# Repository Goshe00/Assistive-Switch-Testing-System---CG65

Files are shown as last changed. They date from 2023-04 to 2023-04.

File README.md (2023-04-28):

 <!--- 
TITLE
Should match the name of the GitHub repository. Choose something descriptive rather than whimsical. 
 --->
 # Assistive Switch Testing System - CG65

<!--- 
SUMMARY
A brief summary of the project. What it does, who it is for, how much it costs.
 --->
We are from UBC ECE Capstone Group CG65 and our project is to build a cost-effective test system for engineers to test the assistive switch for Neil Squire's Program Makers Making Change. The testing system is made from modifying a commercially available 3D printer, low cost electrical components, 3D printed parts and specially designed user interface.

<!--- 
PHOTO

 --->
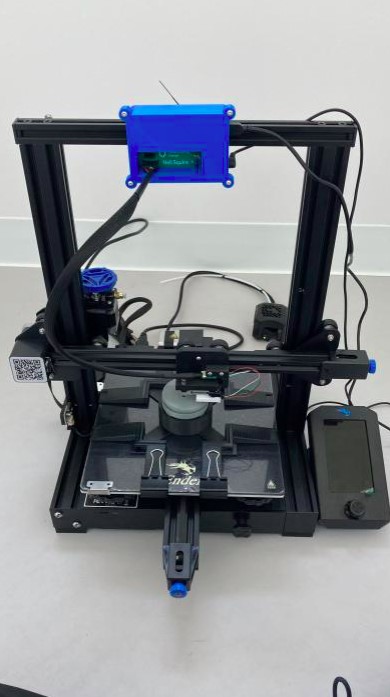
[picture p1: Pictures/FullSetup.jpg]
Assistive Switch Testing System Full Setup


<!--- 
## More info at
 - [Makers Making Change Forum Thread](TBD) 
 - [Makers Making Change Project Page](TBD)
 --->

## Getting Started
<!--- 
Include an overall idea of what major steps are required to build the device.
 --->

### 1. Order the 3D printer
Our testing system will be assembled on a 3D printer. For our project, we've chosen the Ender 3 V2 from [3D Printing Canada](https://3dprintingcanada.com/products/creality-ender-3-v2) since it is CSA and ETL safety certified. So far, this testing system has been implemented on an Ender 3 V2 and you can acquire the same model from any available store.

### 2. Order and assemble the activation circuit
The activation circuit will be used to receive and send signals from the load cell and switch to a computer.

All of the files and documentation can be found in the [/Electronics/Activation_Circuit/PCB_Assembly_Guide.pdf](https://github.com/Goshe00/Assistive-Switch-Testing-System---CG65/tree/main/Electronics/Activation%20Circuit) folder.

### 3. Order and assemble the force sensor

The force sensor includes the load cell and its adapter. It will be used to send signals to the PCB during a testing routine.

All of the documentation can be found in the [/Electronics/Force Sensor](https://github.com/Goshe00/Assistive-Switch-Testing-System---CG65/tree/main/Electronics/Force%20Sensor) folder. Individual print files of the adapter can be found in [/3D_Printing_Files/Load_Cell_Adapter](https://github.com/Goshe00/Assistive-Switch-Testing-System---CG65/tree/main/3D%20Printing%20Files/Load%20Cell%20Adapter) folder. The code to configure the microcontroller can be found in [/Software/ESP](https://github.com/Goshe00/Assistive-Switch-Testing-System---CG65/tree/main/Software/ESP32)

### 4. Install and setup Neoprint, our testing system's user interface

Neoprint is a Python program specifically for this testing system that enables the user to set up, run test routines and generate data. 

All of the build documentation and files can be found in the [/Software/Neoprint](/Software/Neoprint) folder. 

### 5. Assemble the force sensor, activation circuit and Neoprint

After assembling and setting up each of the subcomponents, they can be assembled together to build the testing system.

User guides of each subcomponents can be found in their respective folders. 

### 6. Assemble the switch 

The testing procedure starts by deciding which switch is needed to be tested. For this project, we have implemented a testing procedure for the MMC60 switch. 

### 7. Print and assemble the switch adapter

In order for the switch to be fixed on the printbed, an adapter is needed to hold the switch so that it does not move or rotate during testing.

All individual print files and documentation of MMC60 switch and Interact switch can be found in [/3D_Printing_Files/MMC60_Jig](https://github.com/Goshe00/Assistive-Switch-Testing-System---CG65/tree/main/3D%20Printing%20Files/MMC60%20Jig) folder and [/3D_Printing_Files/Interact_Switch_Jig](https://github.com/Goshe00/Assistive-Switch-Testing-System---CG65/tree/main/3D%20Printing%20Files/Interact%20Switch%20Jig) folder.

### 8. Run testing routine

Now that the testing system is assembled and a switch to test has been chosen, you are ready to run a test!

The detailed testing routine instructions can be found at [/Software/Neoprint](/Software/Neoprint).

## Future Works

### 1. Locking jigs for other types of assistive switches

For this project, we only focused on building and testing the MMC60 Switch and Interact Switch. The testing routine requires a specific locking jig design for different types of switches. We have developed a Locking Jig Design Guide in [/3D Printing Files](https://github.com/Goshe00/Assistive-Switch-Testing-System---CG65/blob/main/3D%20Printing%20Files/Locking%20Jig%20Design%20Guide.pdf) for future developments of other types of locking jig designs. 

### 2. Button profiles for other types of assistive switches

The software requires the dimensions of the button to automatically generate testpoint locations. The current code uses the dimension of the MMC60 button (60mm diameter and 45.7mm height). To test other cylindrical buttons, the variables "BUTTON_MAX_COORD" and "self.window_size" in mode_window_layout.py would need to be changed to the diameter (in mm) of the button, and "45.7" in the method send_gCode_Test would need to be changed to the height (in mm). Adding button profiles would make it easier for testing without having to edit the code each time we want to test a new button. A possible implementation is giving the user the option to add a new button profile (dimensions) or select from a previously saved profile. 

## License
<!---
LICENSE
Choose an appropriate license. We recommend an open-source hardware compatible license.
--->
Everything (excluding Ender 3 V2) needed or used to design, make, test, or prepare the Assistive Switch Testing System is licensed under the CERN 2.0 Weakly Reciprocal license <https://ohwr.org/project/cernohl/wikis/Documents/CERN-OHL-version-2> (CERN-OHL-W).

Accompanying material such as instruction manuals, videos, and other copyrightable works that are useful but not necessary to design, make, test, or prepare the Assistive Switch Testing System are published under a Creative Commons Attribution-ShareAlike 4.0 license <https://creativecommons.org/licenses/by-sa/4.0/> (CC BY-SA 4.0).

## Attribution
<!---
ATTRIBUTION
Include any information related to the development of the design. This may include who identified the initial challenge, who contributed to the design
--->

The documentation template was created by Makers Making Change and is used under a CC BY-SA 4.0 license. It is available at the following link: https://github.com/makersmakingchange/OpenAT-Template

## About Makers Making Change
Makers Making Change Logo

Makers Making Change is an initiative of [Neil Squire](https://www.neilsquire.ca/), a Canadian non-profit that uses technology, knowledge, and passion to empower people with disabilities.

We are committed to cultivating a network of volunteer makers who support people with disabilities in their communities through cost effective assistive technology. Check out our library of free, open-source assistive technologies.

 - Website: [www.MakersMakingChange.com](https://www.makersmakingchange.com/)
 - [GitHub](https://github.com/makersmakingchange)
 - [Thingiverse](https://www.thingiverse.com/makersmakingchange/about)
 - Twitter: [@makermakechange](https://twitter.com/makermakechange)
 - Instagram: [@makersmakingchange](https://www.instagram.com/makersmakingchange)

### Contacts
For technical questions, to get involved, or to share your experience we encourage you to visit [MMC Forum](https://forum.makersmakingchange.com) or contact info@makersmakingchange.com

## About UBC ECE Capstone CG65

We are a group of five Electrical Engineering students that are enrolled in the UBC ECE Capstone program. Our capstone group includes:

1. Daniel Wu, developer of NeoPrint and testing routine
2. Karat Wannissorn, assisted in documenting and developing NeoPrint
3. Henry Bryant, designed button activation circuit and force sensor
4. Sean Fu, assisted in researching force sensor alternatives
5. Shadeed Lagani, designed 3D models and researched locking jigs 

### Contacts
For technical questions, contact ubcece65neilsquire@gmail.com

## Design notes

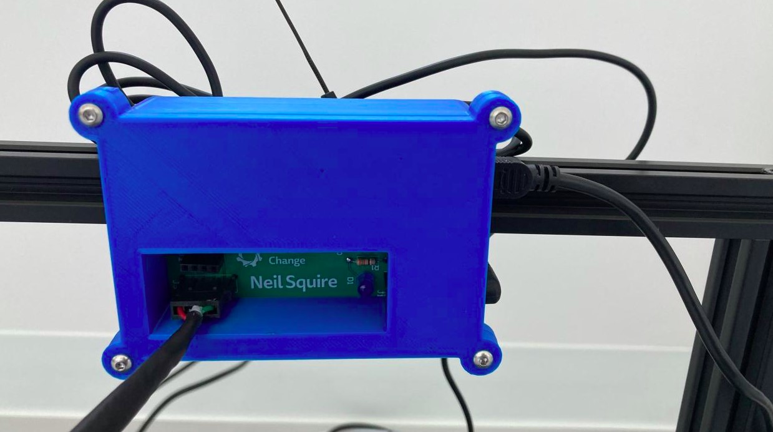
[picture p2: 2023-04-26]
Pictures/PCB.jpg

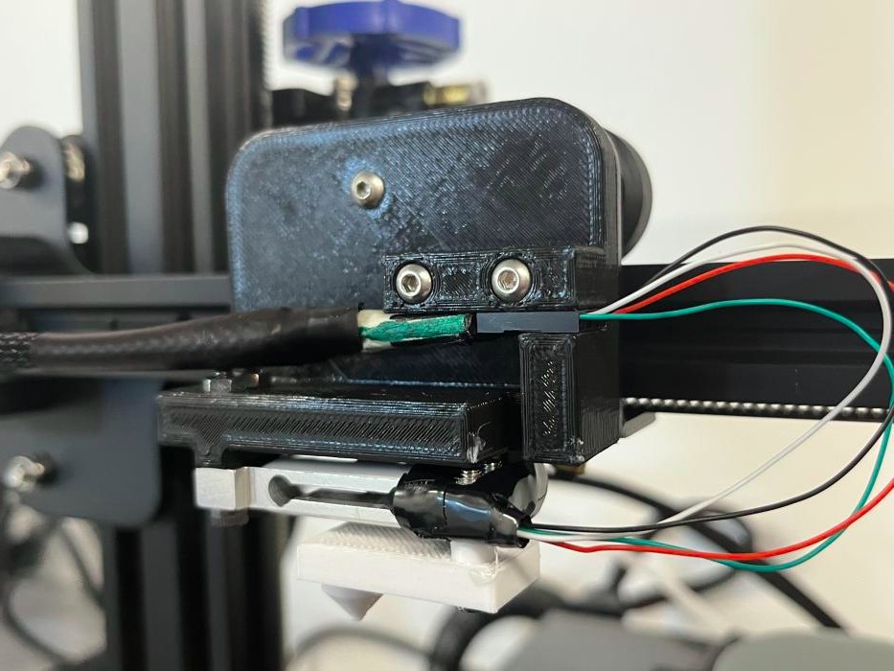
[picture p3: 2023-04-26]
Pictures/LoadCellAdapter.jpg

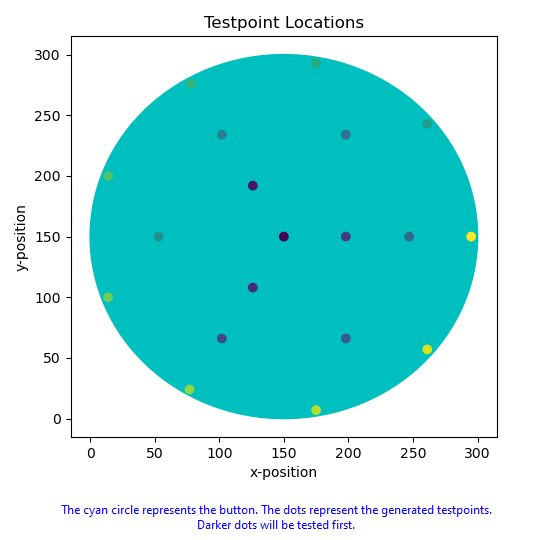
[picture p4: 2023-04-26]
Software/generated_rings.png

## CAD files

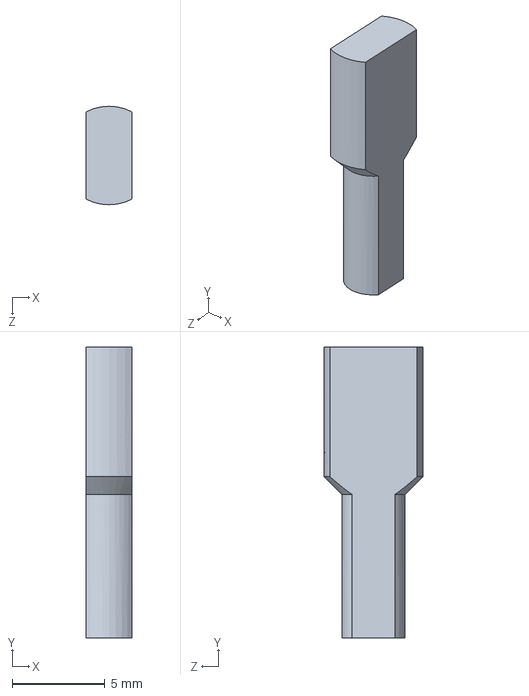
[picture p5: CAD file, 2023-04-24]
3D Printing Files/Interact Switch Jig/PART/JigSnapsV2.SLDPRT
2.50 x 15.7 x 5.32 mm

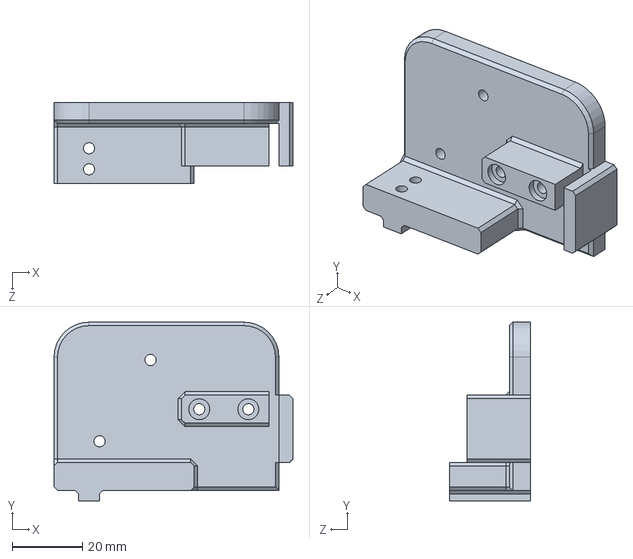
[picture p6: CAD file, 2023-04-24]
3D Printing Files/Load Cell Adapter/PART/LoadCell_AdapterV2 .SLDPRT
68.2 x 51.0 x 23.0 mm

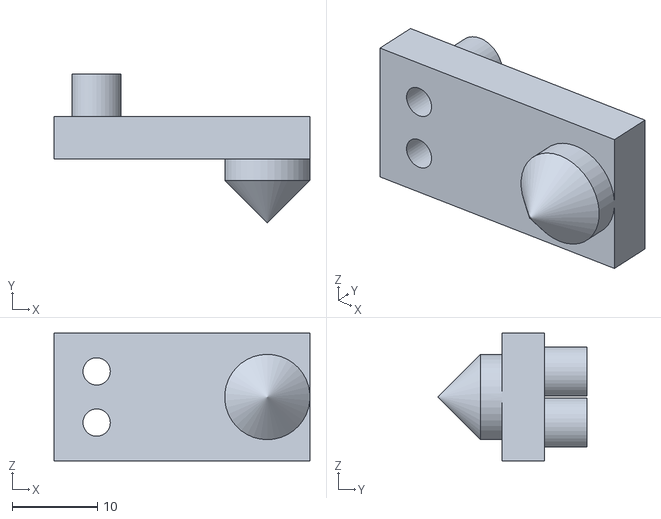
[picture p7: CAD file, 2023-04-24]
3D Printing Files/Load Cell Adapter/STL/LoadCell_Probe .STL
30.0 x 17.5 x 15.0

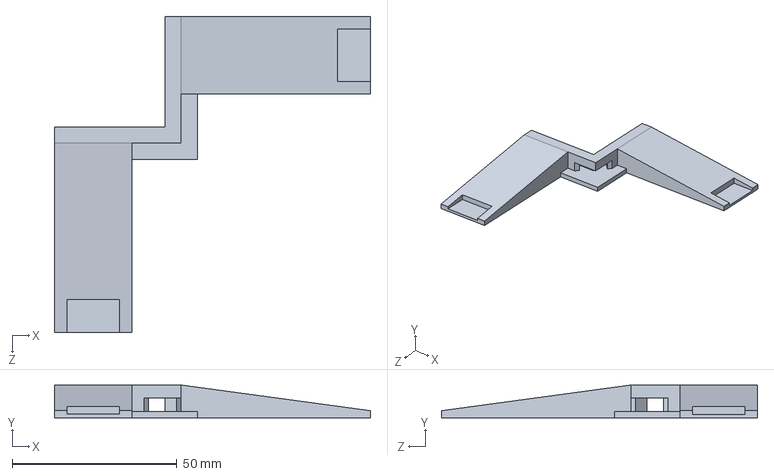
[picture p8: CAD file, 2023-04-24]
3D Printing Files/MMC60 Jig/PART/JigPrintbedAdapter.SLDPRT
96.0 x 10.0 x 96.0 mm

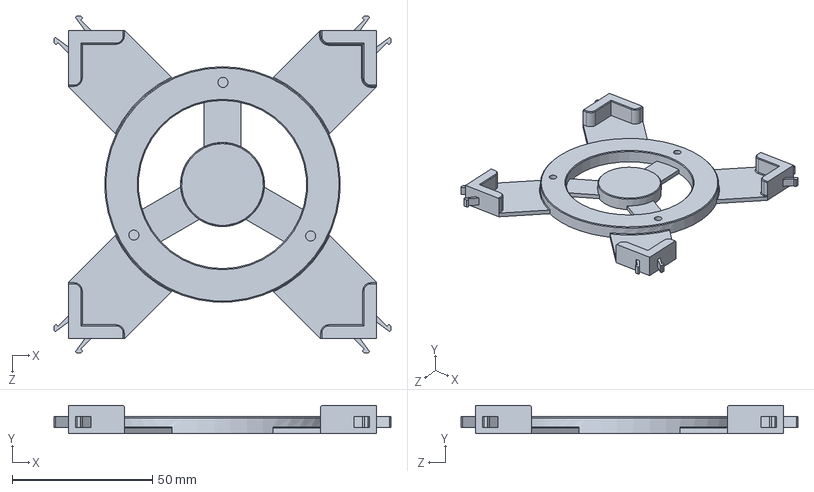
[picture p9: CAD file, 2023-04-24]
3D Printing Files/Interact Switch Jig/PART/InteractJigV2.SLDPRT
120.2 x 10.0 x 120.2 mm

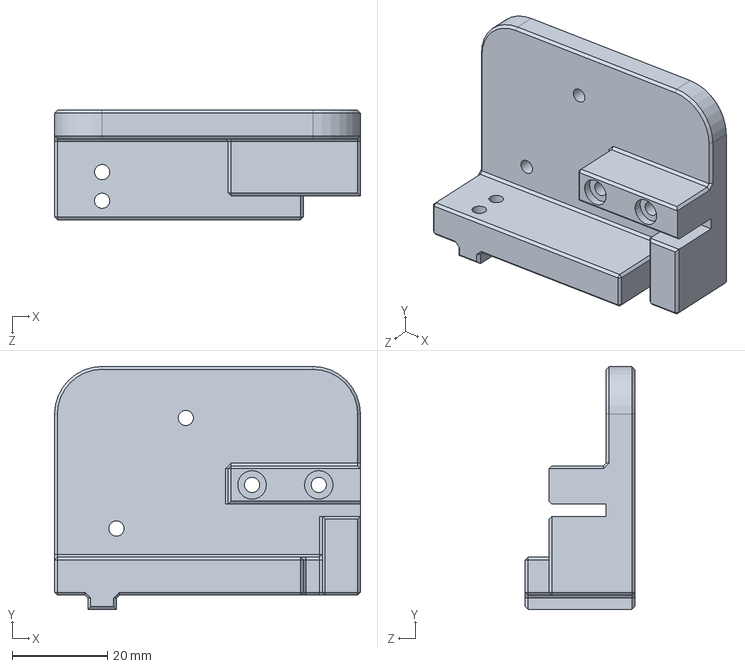
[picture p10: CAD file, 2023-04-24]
3D Printing Files/Load Cell Adapter/PART/LoadCell_Adapter.SLDPRT
64.2 x 51.0 x 23.0 mm

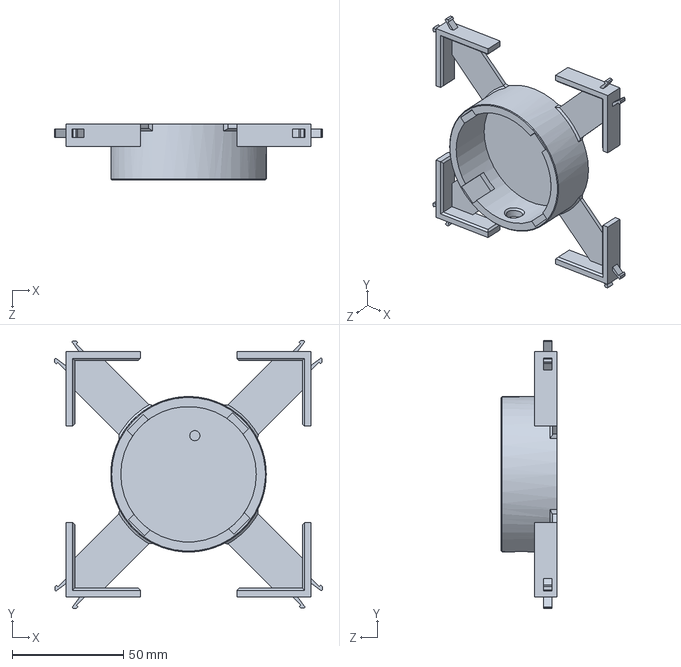
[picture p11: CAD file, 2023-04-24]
3D Printing Files/MMC60 Jig/PART/MMC60_Jig.SLDPRT
120.6 x 120.6 x 25.0 mm

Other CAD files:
3D Printing Files/Interact Switch Jig/STL/InteractJigV2.STL
3D Printing Files/Interact Switch Jig/STL/JigSnapsV2.STL
3D Printing Files/Load Cell Adapter/STL/LoadCell_Adapter.STL
3D Printing Files/Load Cell Adapter/STL/LoadCell_AdapterV2.STL
3D Printing Files/MMC60 Jig/STL/JigPrintbedAdapter.STL
3D Printing Files/MMC60 Jig/STL/MMC60_Jig.STL

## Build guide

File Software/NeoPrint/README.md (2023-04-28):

# README

# NeoPrint

## Testing Routine 

After setting up the hardware...

### Single Test-point Mode 



1. Run main_window.py
2. Select "Single-point test"
3. Select the port connected to the 3D-printer [1] (see Device Manager > Ports)
4. Select a baud rate of 115200 [2] and press Connect
5. Select the port connected to the microcontroller [3] (see Device Manager > Ports)
6. Select a baud rate of 115200 [4]  and press Connect 
7. Enter the x coordinate of the desired test position [6]
8. Enter the y coordinate of the desired test position [7]
9. Press Generate [8] 
10. Press TESTBY [9]
11. Wait for the test to complete and view results on the bottom right [10]

### Multi Test-point Mode 



1. Run main_window.py
2. Select "Multi-point test"
3. Select the port connected to the 3D-printer [1] (see Device Manager > Ports)
4. Select a baud rate of 115200 [2] and press Connect
5. Select the port connected to the microcontroller [3] (see Device Manager > Ports)
6. Select a baud rate of 115200 [4]  and press Connect 
7. Choose to either generate points in rings or scattered points [6]
8. Select the number of rings or the number of points depending on the option selected in step 8 [7]
9. Press "Generate" [8]
10. Press "TESTBY" [9]

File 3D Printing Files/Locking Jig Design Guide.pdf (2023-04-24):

# Jig Design Guide

The locking system fixes the button-in-test on the system’s ‘bed’ to prevent movement of the

button-in-test that will contribute to errors during testing. Specifically, as a probe is lowered

down over different points of the button-in-test, it is crucial to have the button-in-test fixed so

that measurements would remain accurate.

## Existing Design Justifications

### Printbed Adapter

The adapters create a space in which the jig can be placed on. Its design must be able to align with the edges of the printbed to ensure that the jig is centered.

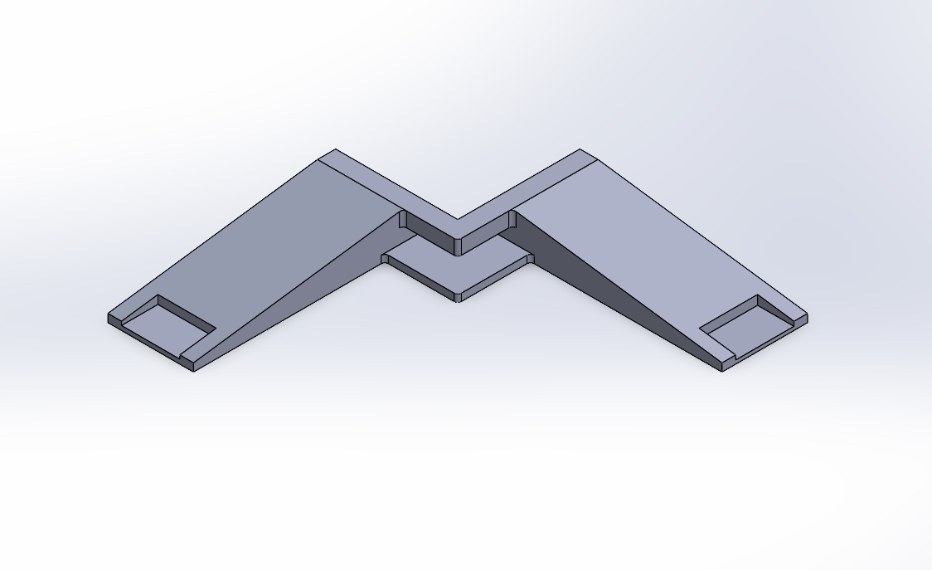
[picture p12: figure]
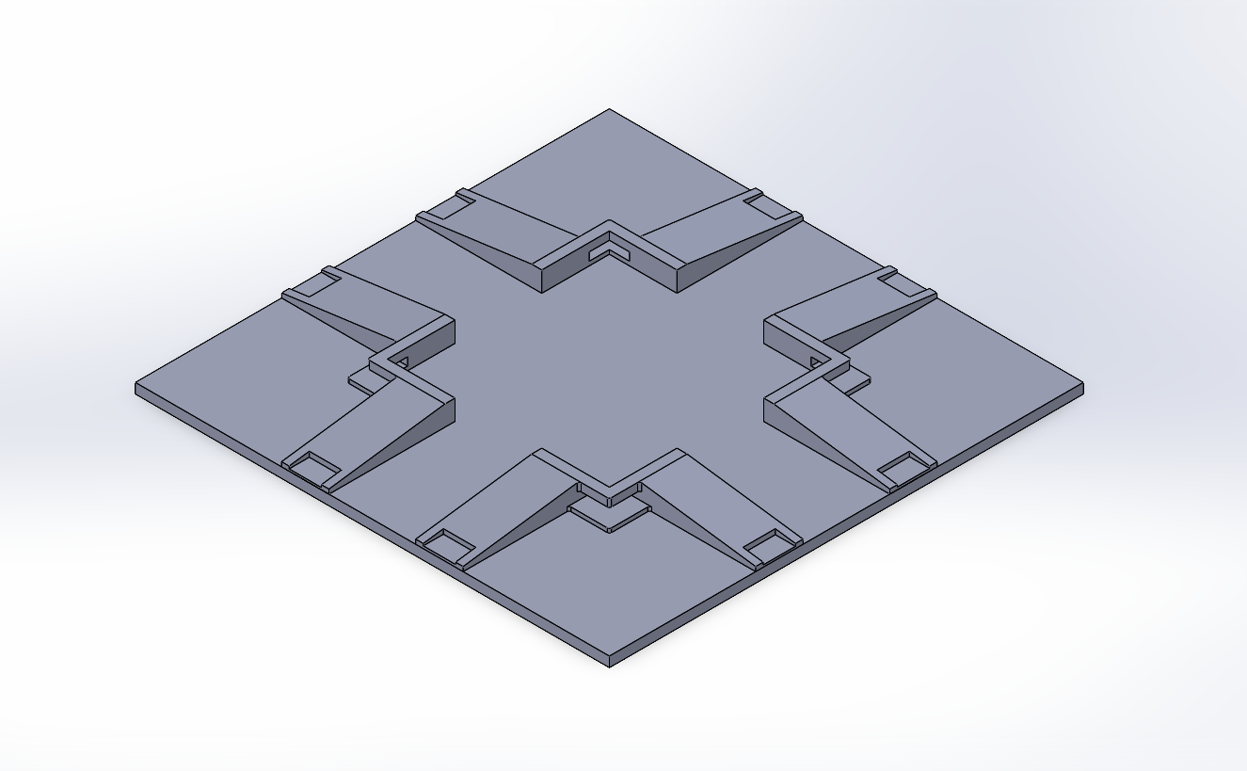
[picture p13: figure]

Individual adapter design | Combination of adapters

Figure: W design with reinforced structure

This design uses a snap fit mechanism to attach the jig to the adapters.

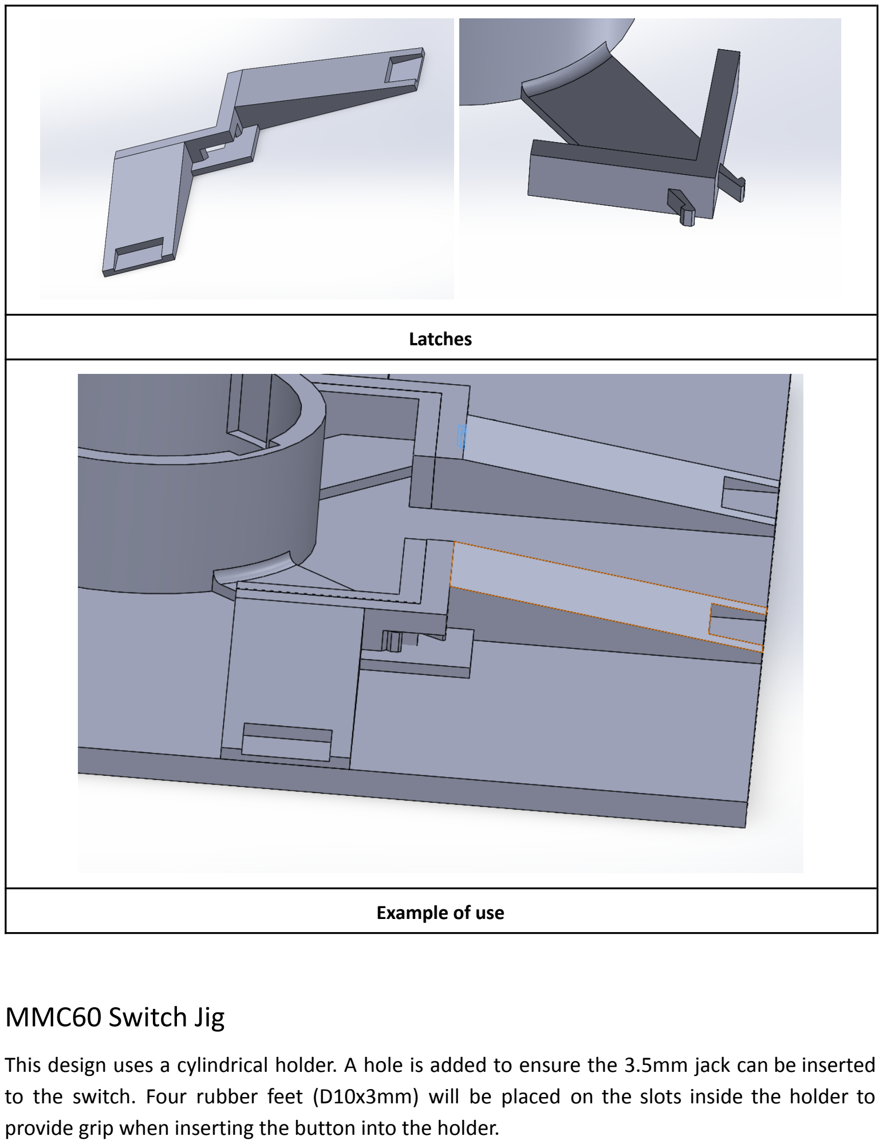
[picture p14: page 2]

Latches

Example of use

### MMC60 Switch Jig

This design uses a cylindrical holder. A hole is added to ensure the 3.5mm jack can be inserted to the switch. Four rubber feet (D10x3mm) will be placed on the slots inside the holder to provide grip when inserting the button into the holder.

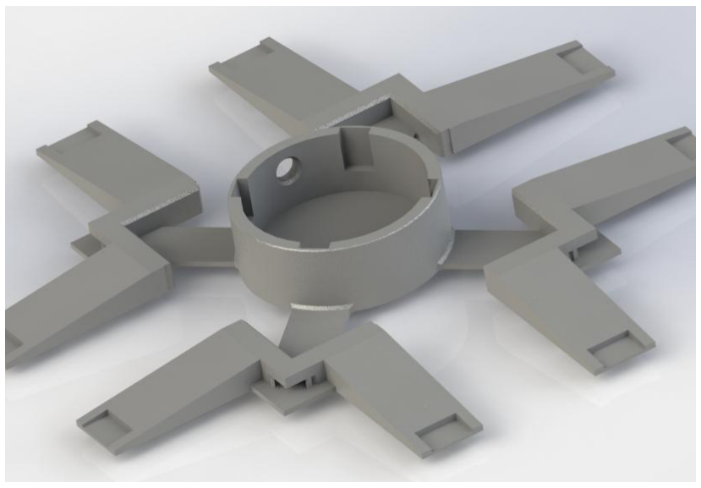
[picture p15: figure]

MMC60 Switch Jig Design

### Interact Switch Jig

This design has two parts, the holder and the cylindrical snaps. The cylindrical snaps are inserted into the holes of the holder. These cylinders will snap to the Interact switch which already includes holes with the same radius

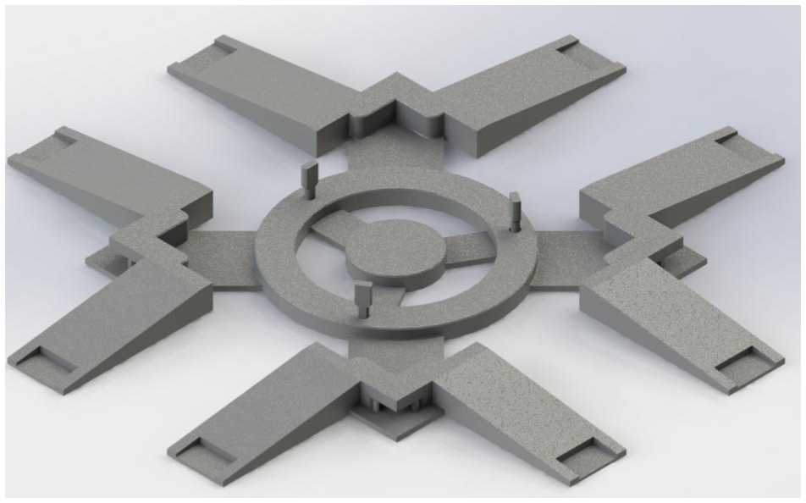
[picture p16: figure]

Interact Switch Jig Design

## Design Approach & Considerations

### Printbed Adapter

When designing the printbed adapter, we need to consider:
1. Edges are aligned to the edges of the printbed
2. Attaching the adapter to the printbed

Attaching the adapter to the printbed can be achieved in two ways:
1. Attaching magnets to the adapter. This requires the printbed to be magnetic, which usually is not
2. Using binder clips to hold the sides. This requires the binder clips to not obstruct the printbed’s movement.

Attaching the adapter to the jigs can be achieved in a few ways, some examples are:
1. Using a lock key. However, this design is flimsy.
2. Using snap fits. This requires careful measurements to ensure a tight fit.

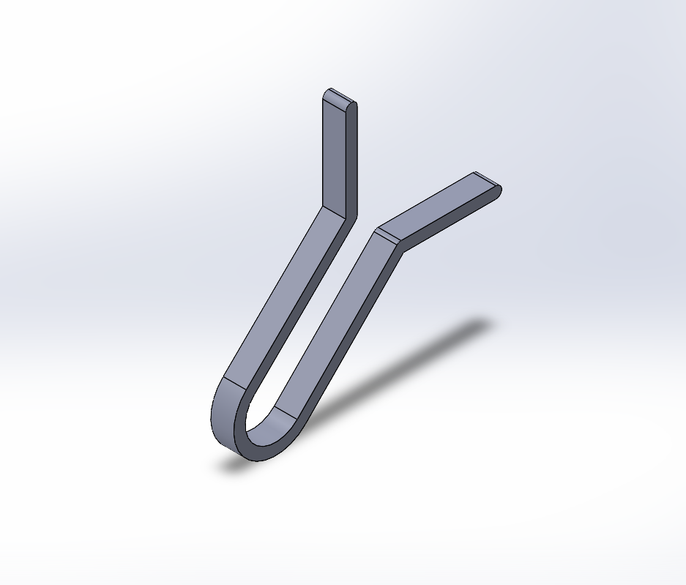
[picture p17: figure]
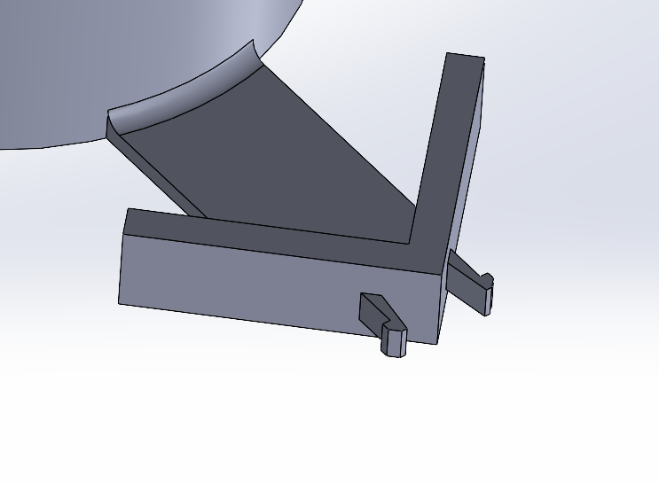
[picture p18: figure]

Individual key design | Individual latch design

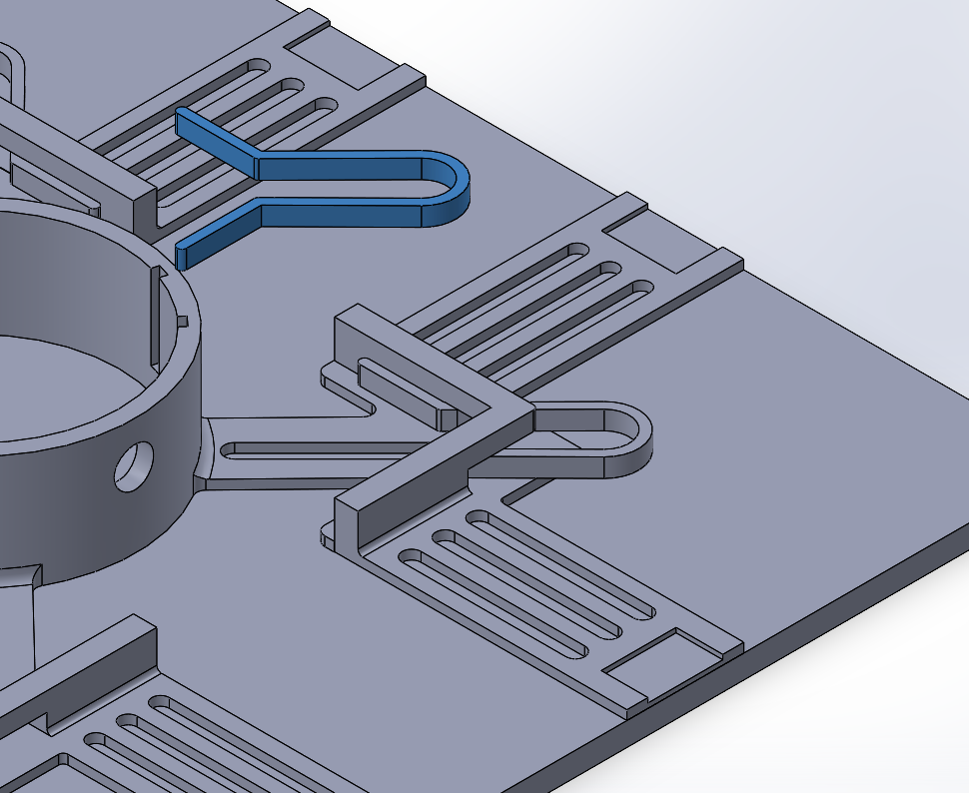
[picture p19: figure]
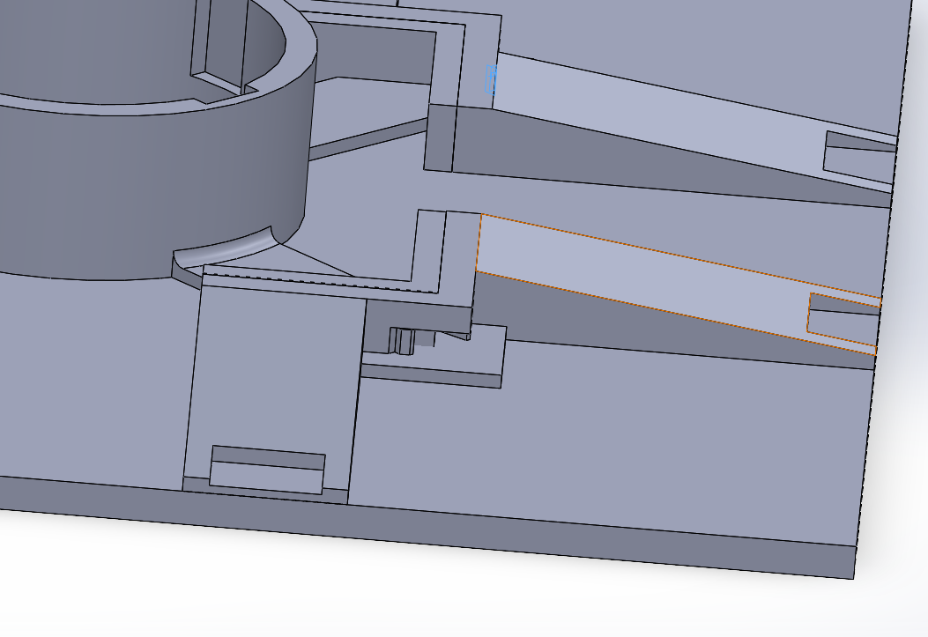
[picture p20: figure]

Example of use (Lock key) | Example of use (latch)

## Locking Jigs

When designing the printbed adapter, we need to consider the shape of the switch and the mounting characteristics of the switch. These two aspects will then deduce how we will design the attachments.

In case of the MMC60, the mounting hole at the bottom is at an off-center position and requires the switch to be screwed into the jig. This leaves us making use of the shape of the switch, which is cylindrical. Thus, we devised a grip option (rubber feet or foam etc.) that will hold the switch on the sides. The jig is also designed so that the jig’s structure is rigid and able to support gripping the switch.

For the Interact switch, the switch already has holes that we can make use of. Thus we devised a design that has cylindrical keys that hold the switch through the switch and the jig’s holes.

Since we also need to consider the printing orientation of the jigs, we need to ensure that the design is rigid and does not break.

## Recommendations

These recommendations are based on judging the shape of the switch, following the design approach of MMC60. The example shows a cross section of the proposed jig design.

Switch | Approach | Example

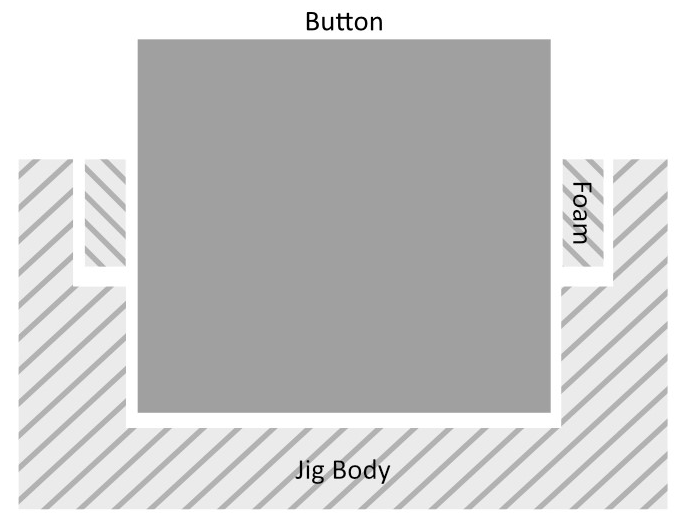
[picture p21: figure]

Volksswitch Accessible Switch | ● Does not have a mounting feature ● Make use of the body of the switch

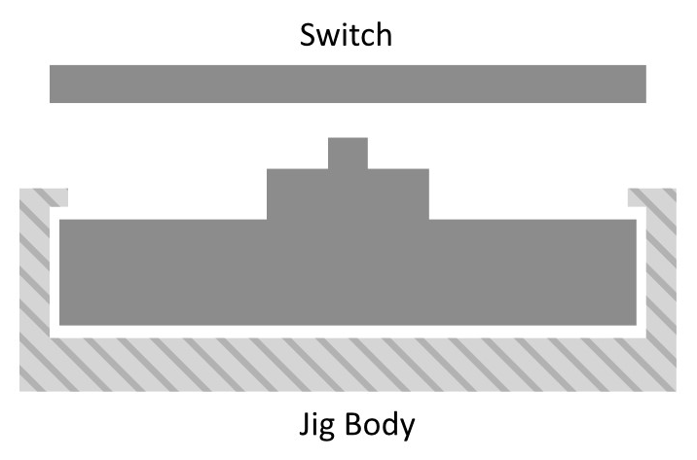
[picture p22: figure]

Solderless Unibody Switch | ● Does not have a mounting feature ● Simple design can be made to ‘slot’ into a jig

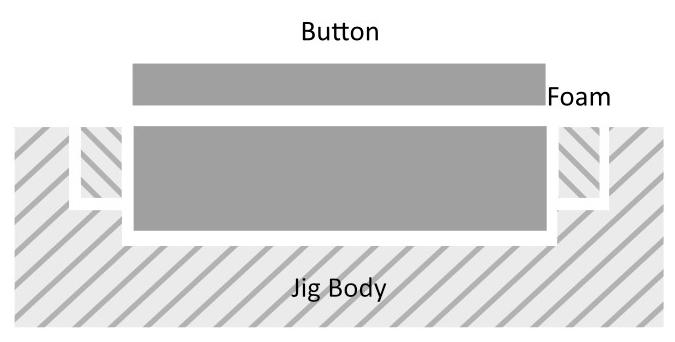
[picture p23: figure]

Light Touch Switch | ● Does not have a mounting feature ● Use foam to grip

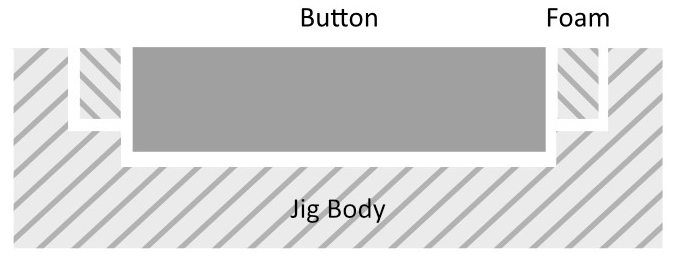
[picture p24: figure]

Raindrop Switch | ● Does not have a mounting feature ● Use foam to grip

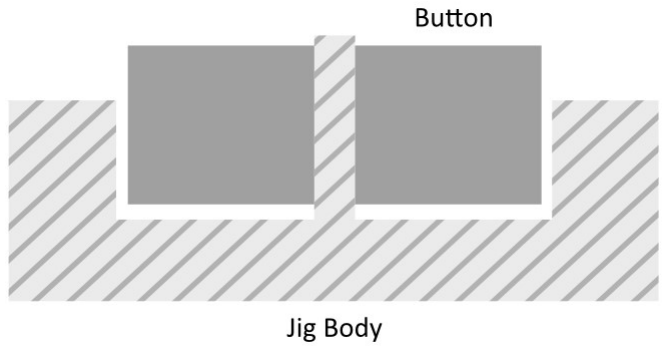
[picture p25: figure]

Lar

g

e Le

ver

Switch

- Ha
v

e

a mounting
featur

e
- The orien
t

ation of the
le

ver should be
positioned so tha

t
parts of the

switch
does not ob

struct
e

xtruder/load cell
adap

ter

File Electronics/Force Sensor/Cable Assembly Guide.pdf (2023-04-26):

# Cable Assembly Guide

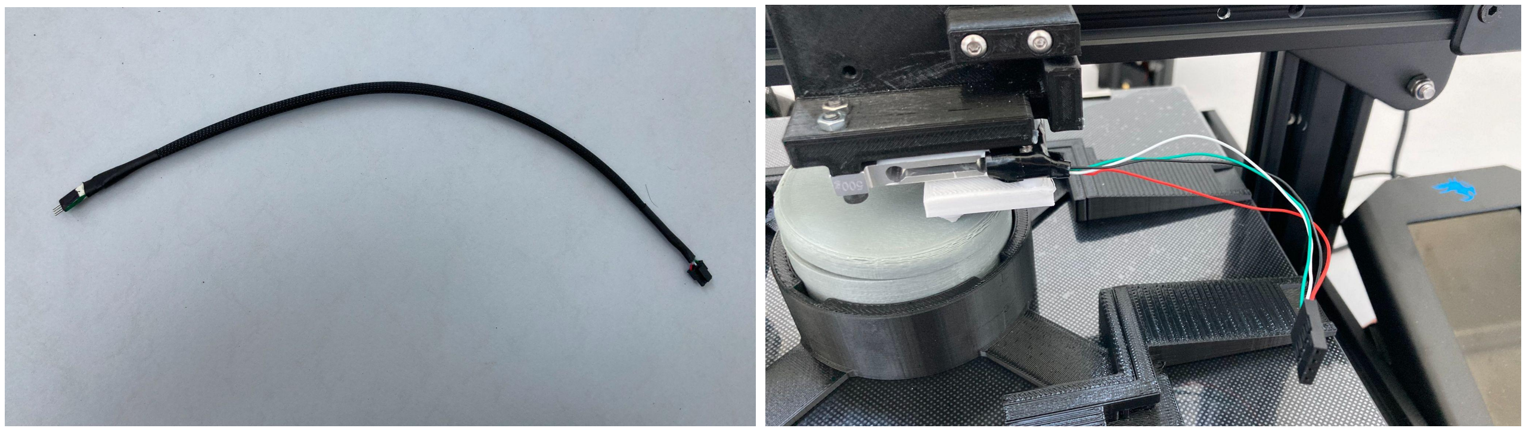
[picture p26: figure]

Inter-Connection Cable | Load Cell Cable

# Materials

1 - Load Cell (SEN-14728)
1 - Molex Connector (0436450400)
4 - Molex Crimps (0430300001)
4 - Female Crimps Dupont Connector Type (Standard Jumper wires, use this guide (https://forum.digikey.com/t/dupont-connectors-and-how-to-find-them-from-digi-key/3315) to find them on Digikey)
4 - Male crimps Dupont Connector Type (Standard Jumper wires, use this guide (https://forum.digikey.com/t/dupont-connectors-and-how-to-find-them-from-digi-key/3315) to find them on Digikey)
2 - Dupont Connector Housing (Standard Jumper wire housing, use this guide (https://forum.digikey.com/t/dupont-connectors-and-how-to-find-them-from-digi-key/3315) to find them on Digikey)
1 x 45cm - 22AWG stranded wire
1 x 40cm - ¼” braided sleeving (optional)
2 x 4cm - ¼” heat shrink, recommended to use an adhesive type (optional)

# Instructions

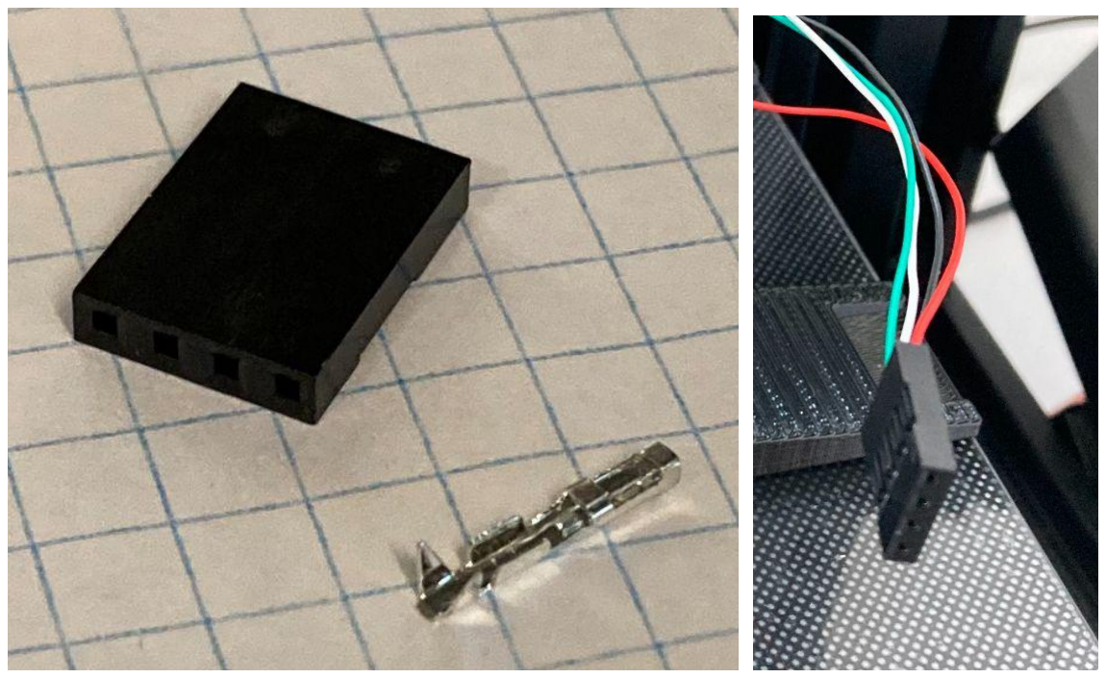
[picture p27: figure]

1. Crimp the female Dupont connector and crimps on the load cell wires using a
crimping tool such as the
following, (https://www.amazon.ca/IWISS-Professional-Compression-Ratcheting-Wire-Electrode/dp/B00OMM4YUY?th=1) using this Tutorial. (https://www.instructables.com/Dupont-Crimp-Tool-Tutorial/) Note since the wires for the load cell are very small, you need to add filler wires to the crimps [such as 24AWG
stranded wire]. With the
filler wire, crimp the
connector and cut off the
excess filler wire with snips.

Be extremely careful with
the load cell wires, since the wires are very prone to
breaking due to the pinch
point on the load cell. It is recommended to add some
strain relief on these wires, however heat is likely not recommended cause it may
damage the load cell.

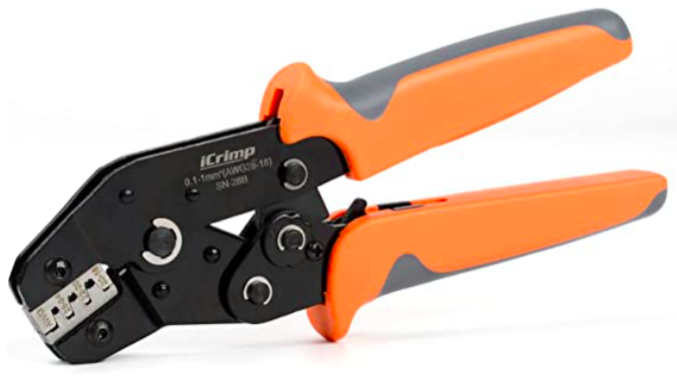
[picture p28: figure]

Order: Green, White, Black, Red

2. Use the 45cm of 22AWG wire and crimp the male Dupont
crimps onto one end of the wires in the (make sure to note the order of wires to match the load cell wires, as shown by the picture). Note this time you will not need filler wire, but you can use the same technique as
before.

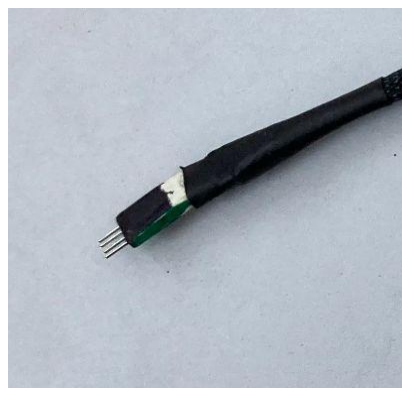
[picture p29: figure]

Order: Green, White, Black, Red

3. If you choose to use the | braided sleeving and heat shrink to protect the wires, you can slip them on at this time. On the jumper wire end, you can use a heat gun or similar means to shrink it, leaving a little bit of room on either end with wires exposed for it to latch on both the wires and the braided sleeving. | From the picture, you can see the heat shrink encompasses both the wires and the braided sleeving.

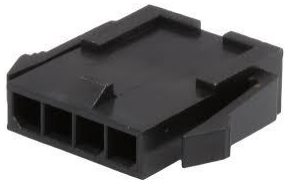
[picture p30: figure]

4. Note, it would be | recommended to change the style of crimp for the dupont type to latch on to the load cell adapter (such as a panel mount connector). A MOLEX branded panel mounted wire to wire connector (0436400400) could be a better way of avoiding damage to the load cell wires if the wires were to be pulled.
5. Now you can add heat shrink | on the other end of the wire, which will be slid down and used later.

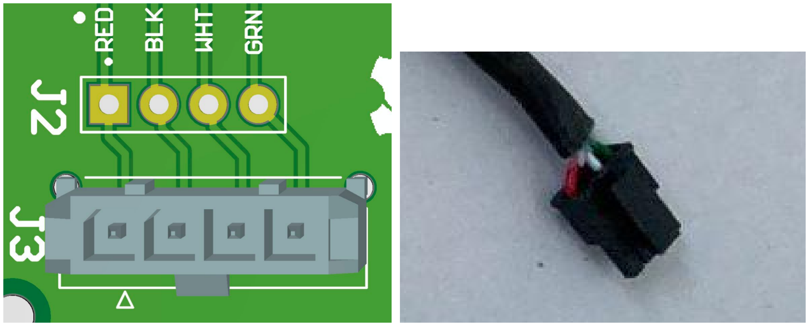
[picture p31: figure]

6. On the other end of the wire, | we will now crimp the Molex connector housing with Molex crimps which will connect to the PCB. On the PCB, the connector is as follows on the right. Note that the order of the connector from the side with the latch (pin 1) is Red, Black,

| White, Green, as shown in the image. In order to crimp these wires, you can follow the same procedure as used for the dupont connectors. Note that the insulation part and wire part of the crimp should be done.
7. You can now move the heat | shrink into position and use a heat gun or similar means to shrink it into position as before on the other end of the wire. Note to keep a little bit of space between the end of the heatshrink and the connector to avoid pinching the wires together too much.

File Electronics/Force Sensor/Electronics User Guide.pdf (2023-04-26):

# Electronics User Guide

# Materials

1 - Assembled PCB

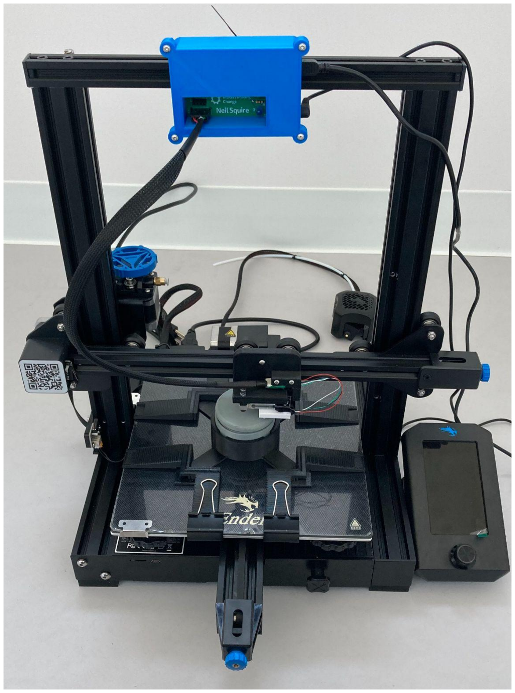
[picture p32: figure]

1 - Assembled Load Cell Cable
1 - Assembled Inter-Connection Cable 1 - 3.5mm jack cable
1 - USB to micro usb cable
1 - Load Cell Mount 3D print
1 - PCB Box Top and Bottom halves 4 - M3 x 14mm Buttonhead screws 4 - M3 Nuts
2 - Zip ties around 10 cm each

## Instructions

1. Make sure to flash the ESP32 (by usb) with the latest code provided under the software portion

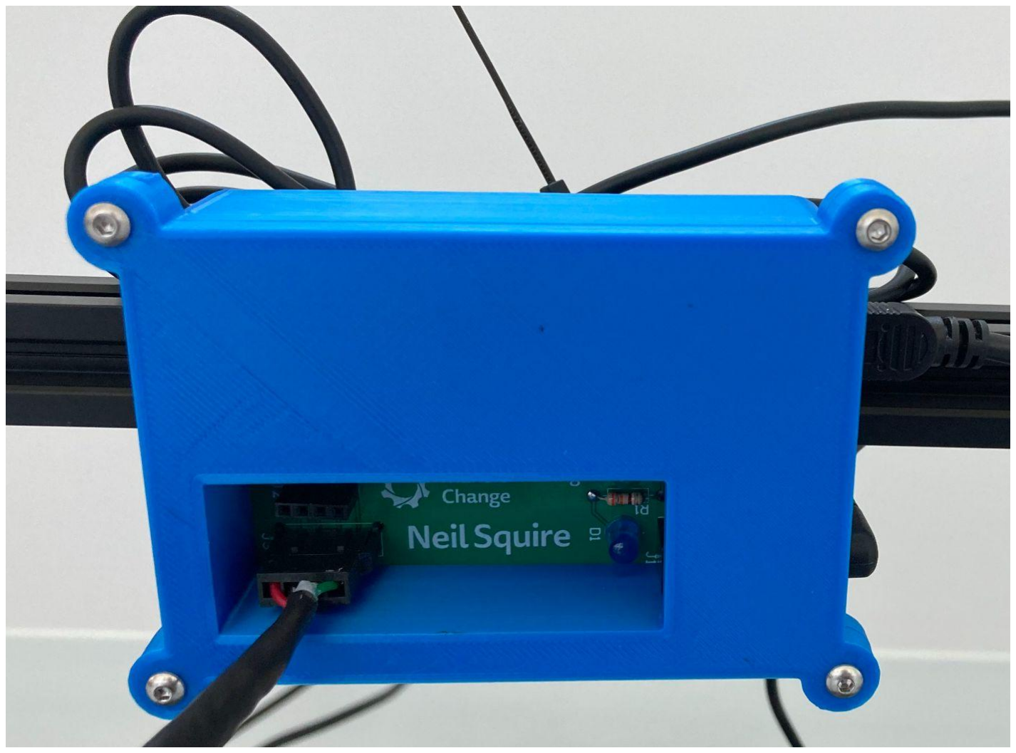
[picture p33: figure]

2. Mount the PCB onto the 2x2cm beam with zip ties through the holes in the back. The PCB should fit snugly between the top and bottom pieces of the 3D printed box, where the top piece fits inside the base and pinches the PCB by 2mm to keep it from slipping out.

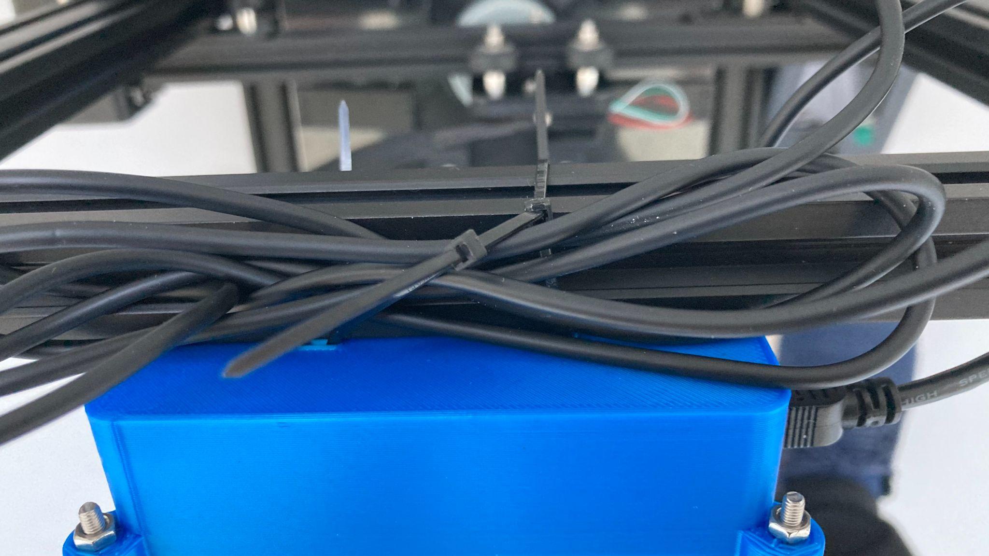
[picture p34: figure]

Plug in the Inter-Connection cable, the USB and the 3.5mm cable to the PCB through the holes provided in the case. You can keep the excess wires of the 3.5mm mono cable at the top if necessary.

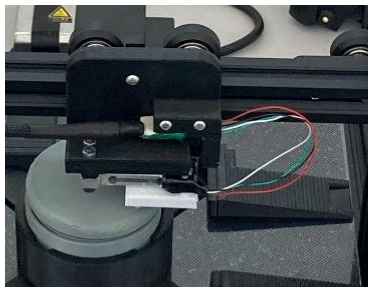
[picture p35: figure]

4. For the Load cell portion, refer to the Load cell Mount assembly guide for this step. Once the load cell mount is mounted to the 3D printer and the load cell is attached, plug in the Inter-Connection cable to the load cell cable. As the Load cell mount guide mentions, you can tuck the dupont connector into the pinch point to keep it from moving.

5. The other end of the 3.5mm mono | cable will be plugged into the button, it is best to plug it in and guide the cable out the back of the printer, attached and guided somewhere to avoid any wire tangles.
6. Doing the same with the USB cable | guiding it to the side it can be plugged into the PC. It is now ready to run the software.

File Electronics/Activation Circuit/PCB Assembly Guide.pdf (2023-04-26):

# PCB Assembly Guide

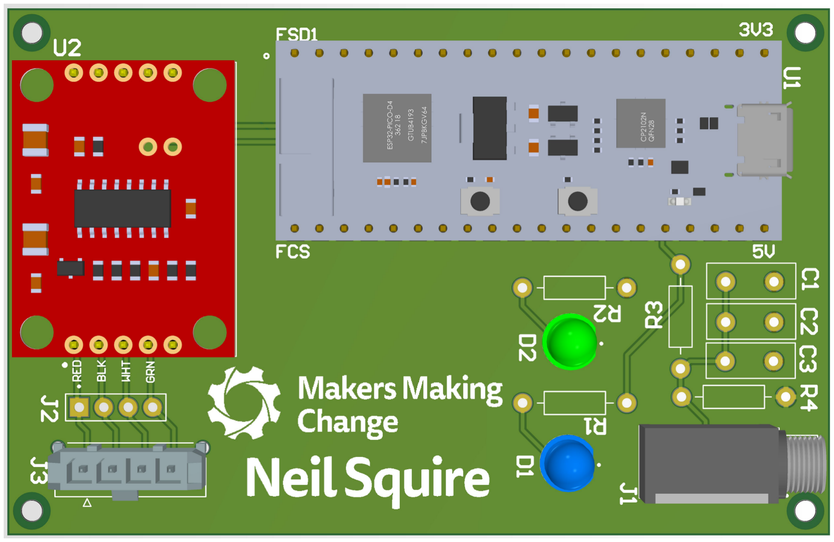
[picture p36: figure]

# Materials

1 - Printed 2 Layer Board (we used JLCPCB, refer to design and gerber files) 1 - ESP32-PICO-D4
1 - Load Cell Amplifier (HX711), part number SEN-13879)
2 - 5x1 Standard 0.1” header (for the amplifier)
1 - Molex 436500427
1 - MJ-3502
1 - LED TH 5mm Blue
1 - LED TH 5mm Green
1 - 0.33uF TH Capacitor (or 3 0.1uF TH capacitors) 1 - 22kΩ TH Resistor
1 - 4.7kΩ TH Resistor
2 - 220Ω TH Resistors

## Instructions

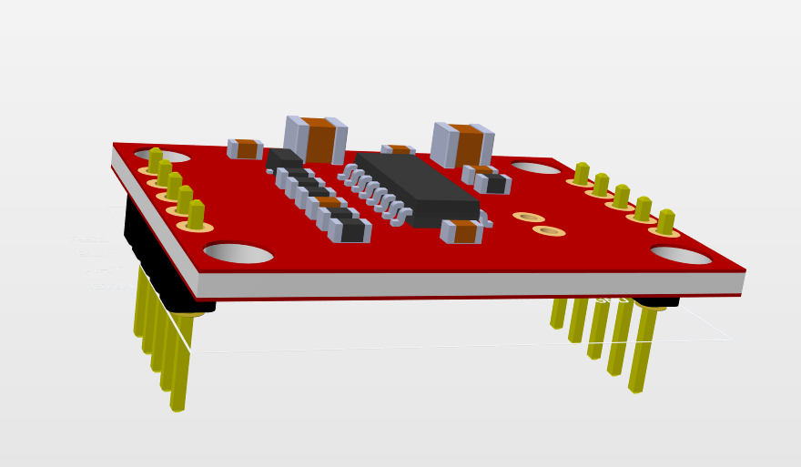
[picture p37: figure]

1. Solder the 5x1 headers
onto the load cell
amplifier (if it does not
come pre-soldered)

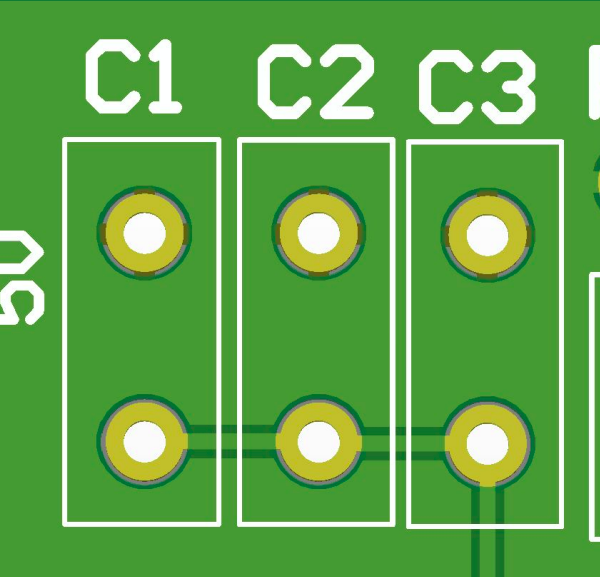
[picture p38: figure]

2. If you are using one
0.33uF capacitor, ignore
the other two pads,
otherwise solder all three 0.1uF capacitors

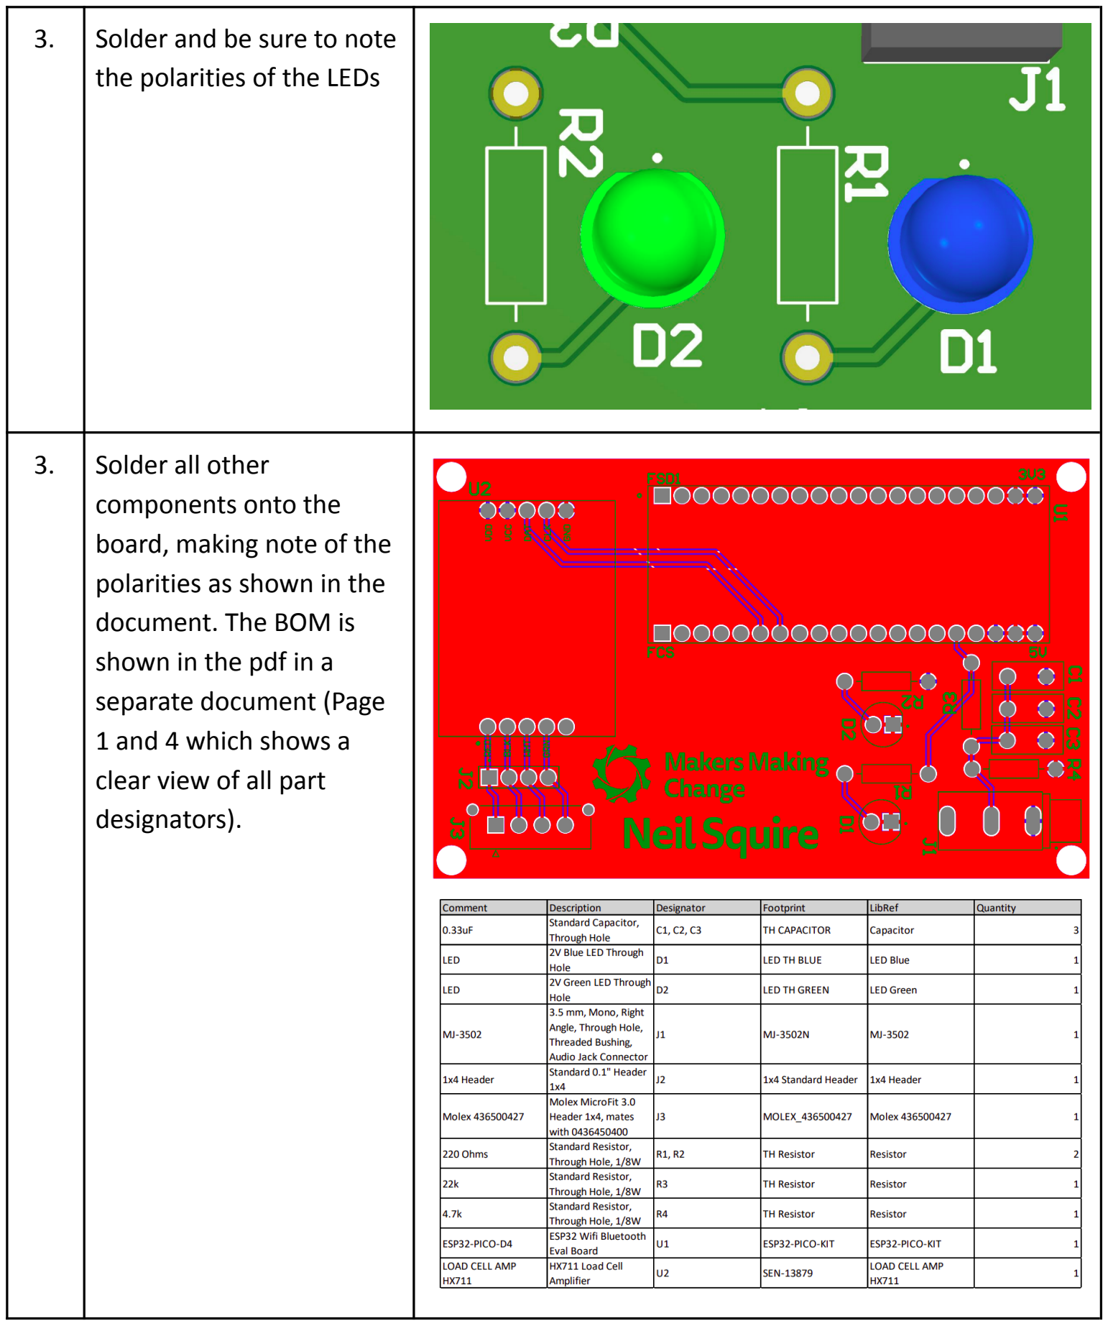
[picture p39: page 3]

3. Solder and be sure to note the polarities of the LEDs
3. Solder all other
components onto the
board, making note of the
polarities as shown in the document. The BOM is
shown in the pdf in a
separate document (Page
1 and 4 which shows a
clear view of all part
designators).

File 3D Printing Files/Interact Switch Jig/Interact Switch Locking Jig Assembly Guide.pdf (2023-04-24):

# Interact Switch Locking Jig Assembly Guide

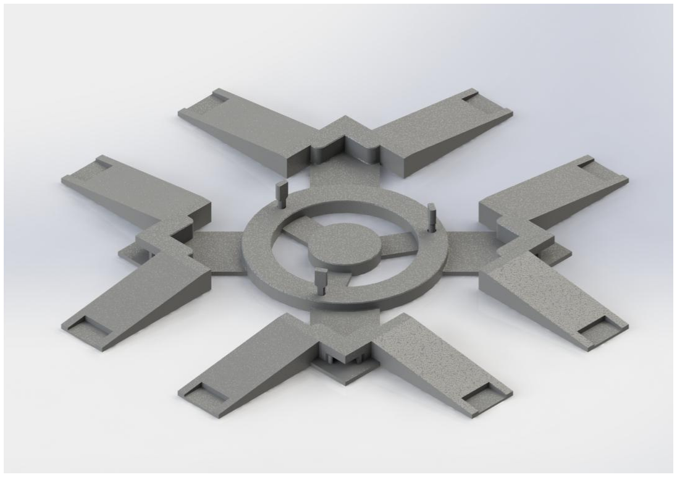
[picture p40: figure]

# Materials

1 - 3D printed Interact Switch Jig
4 - 3D printed printbed adapter
3 - 3D printed Interact Switch Jig snaps

## Instructions

1. Print 3D parts as stated in | the materials

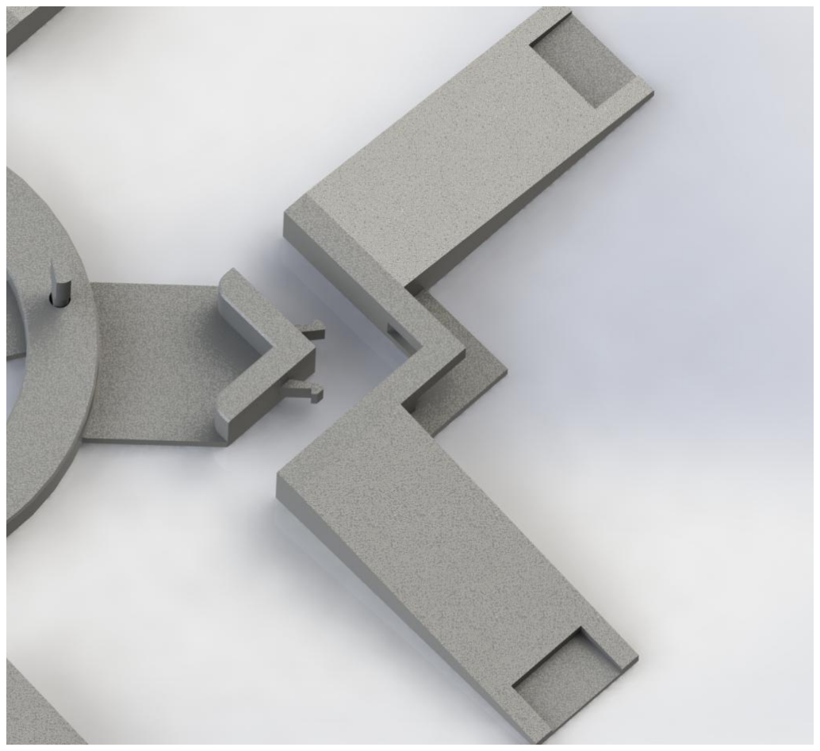
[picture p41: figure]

2. Carefully attach one of the | adapters to the jig’s legs using the snaps
3. Repeat with other | adapters with each legs

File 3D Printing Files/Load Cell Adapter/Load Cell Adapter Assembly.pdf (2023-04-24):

# Load Cell Adapter - Assembly Manual

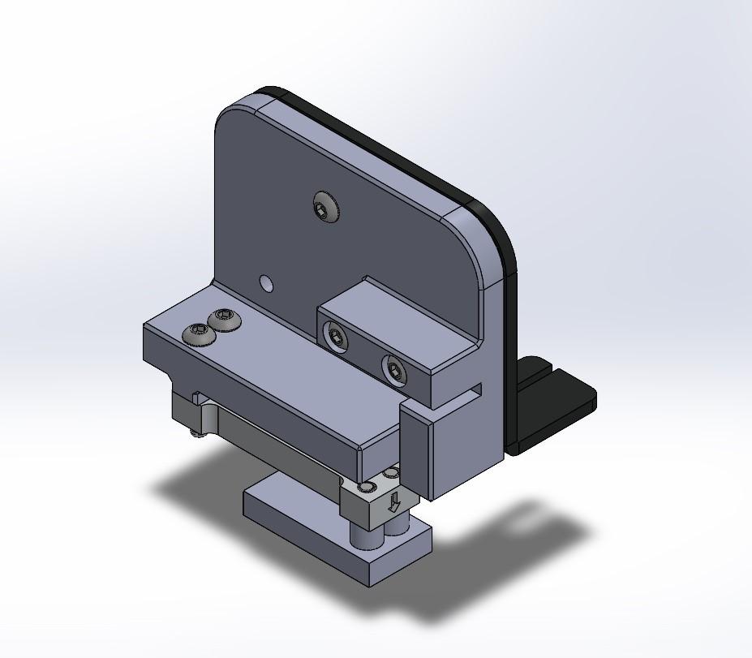
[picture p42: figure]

# Materials

1 - 3D printed adapter
1 - 3D printed probe
1 - Load cell (https://www.digikey.ca/short/pr5hbz4h, $16.49)
4 - M3 x 0.5 20 mm hex drive screw (https://www.mcmaster.com/92095A185/ ) 1 - M3 x 0.5 12 mm hex drive screw (https://www.mcmaster.com/92095A183/ ) 2 - M3 x 0.5 16 mm hex drive screw (https://www.mcmaster.com/92095A184/ ) 3 - M3 x 0.5 hex nut (https://www.mcmaster.com/90592A085/)

# Instructions

## Adapter + Load Cell

1. Remove hot end cover using included | 2mm allen key
3. Remove PTFE tube from the extruder | bracket
4. Mover hot end to the side of the printer

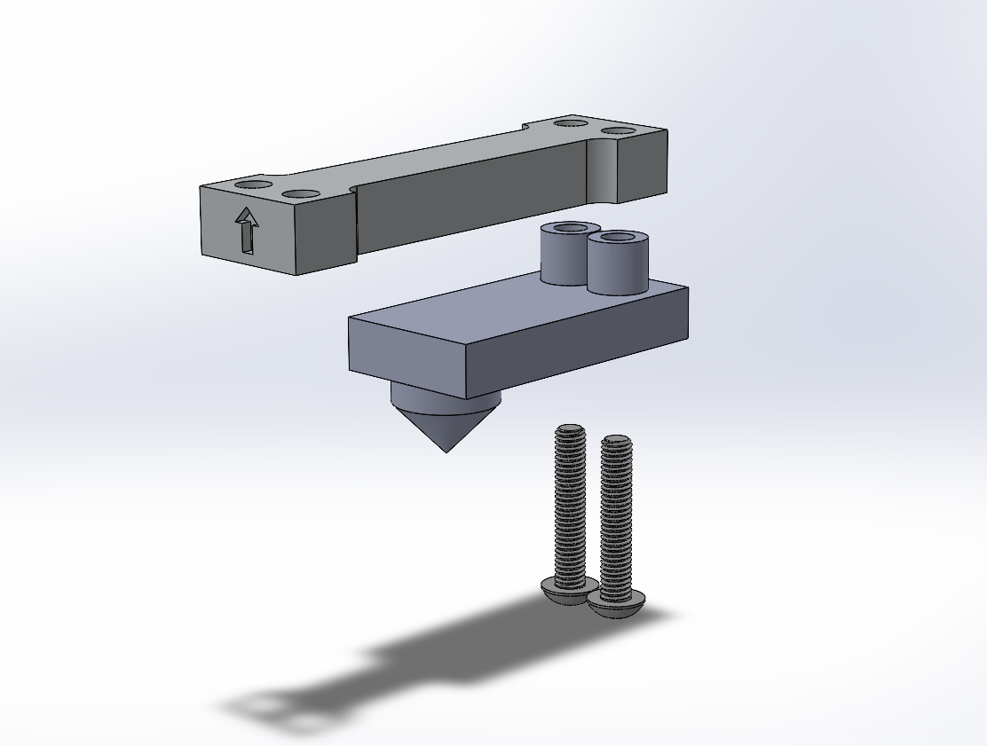
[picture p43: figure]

5. Attach the probe to the load cell using | two M3 16 mm hex drive screws. Ensure that the orientation of the load cell is correct

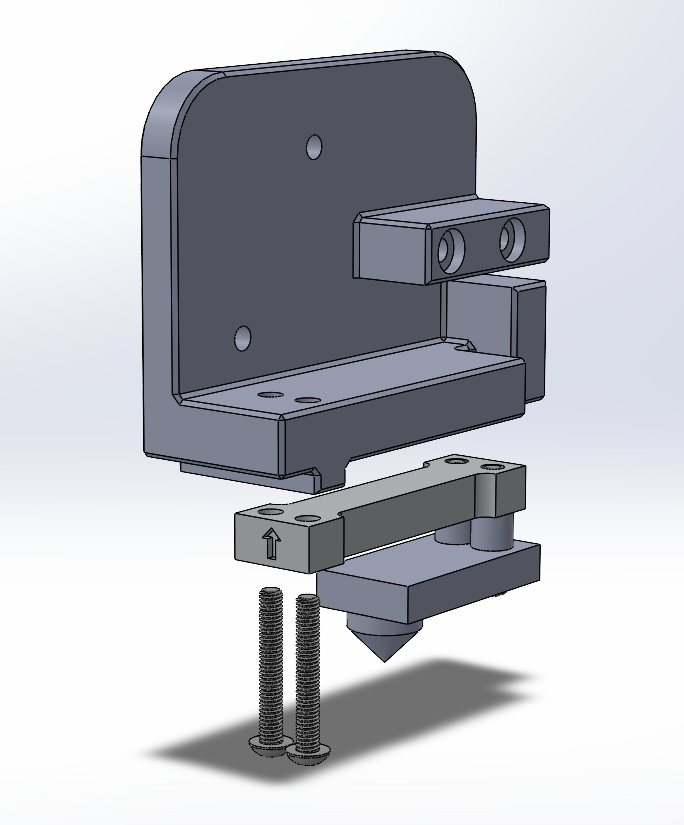
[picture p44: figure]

6. Insert two M3 20 mm hex drive screws into the other side of the load cell, flat side facing upwards.

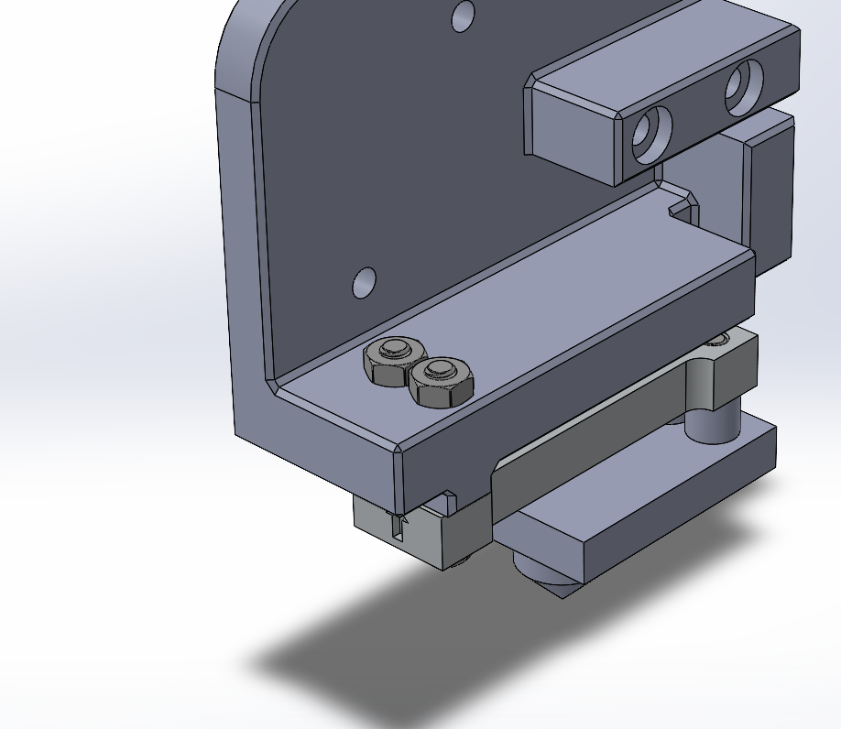
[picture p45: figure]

7. Insert the load cell into the adapter, fixing it with two M3 hex nuts. Ensure that the connections are secure

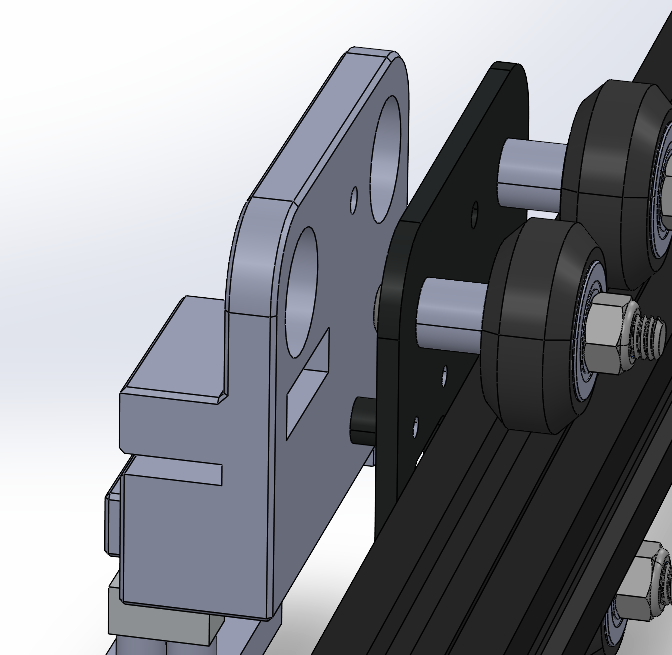
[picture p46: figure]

8. Align the guides into the hot end bracket

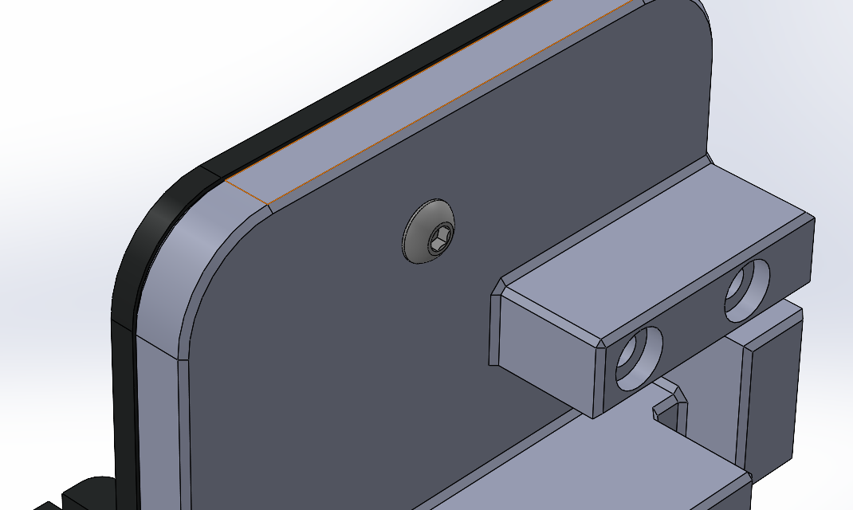
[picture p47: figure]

9. Use a M3 12mm hex drive screw to attach the adapter at the top. Tighten with an M3 nut

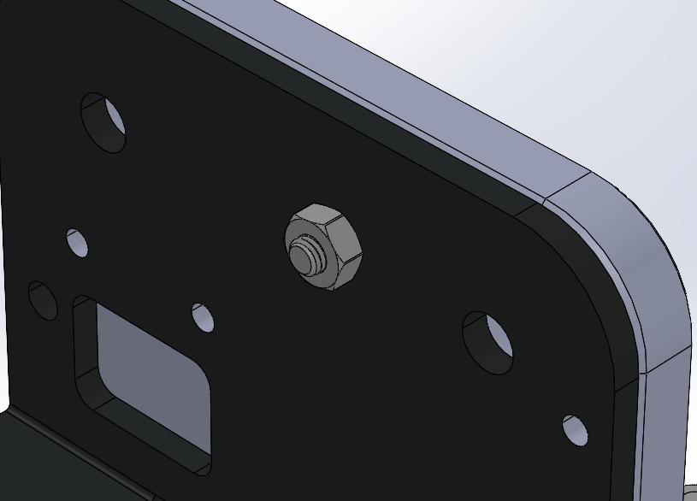
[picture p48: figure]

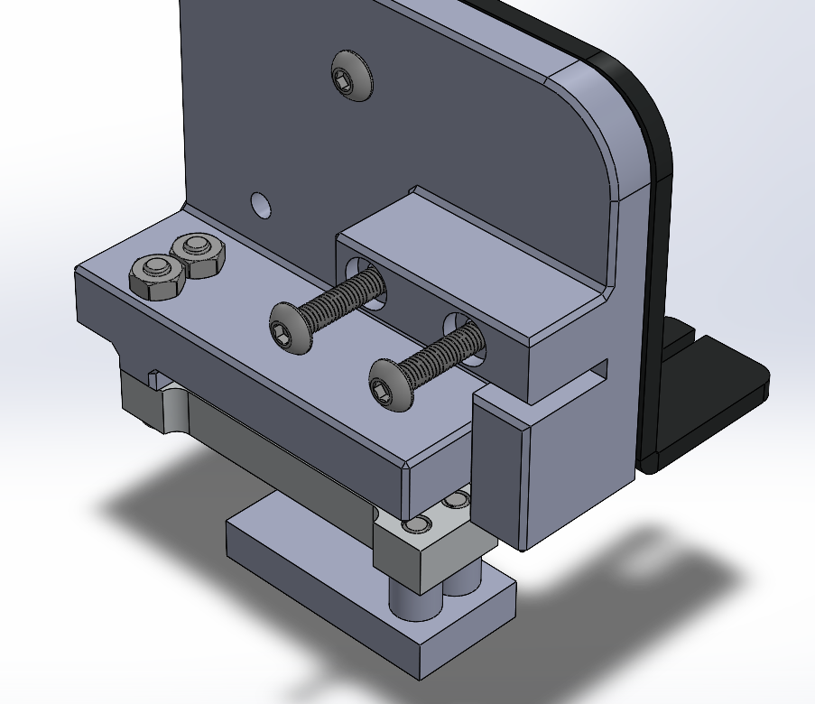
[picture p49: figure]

10. Use two M3 20 mm hex drive screws to | secure the adapter at the right side

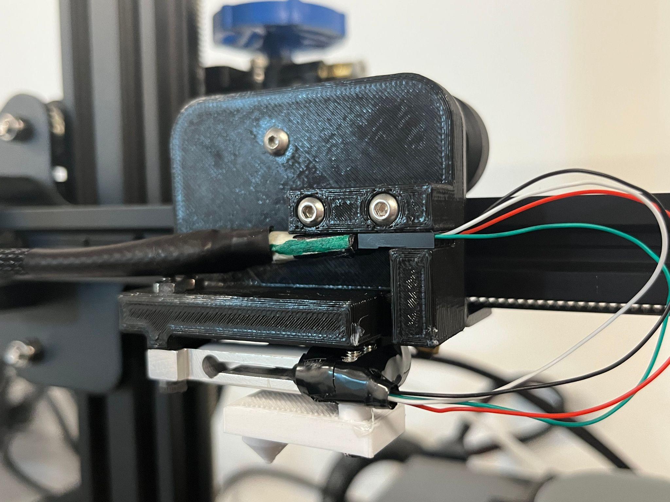
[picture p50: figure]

11. Insert the headers between the spaces | of the adapter. Sand the spaces if the headers does not fit Attach the wires from the PCB to the headers

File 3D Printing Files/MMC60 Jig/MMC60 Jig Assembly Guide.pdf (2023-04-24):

# MMC60 Locking Jig Assembly Guide

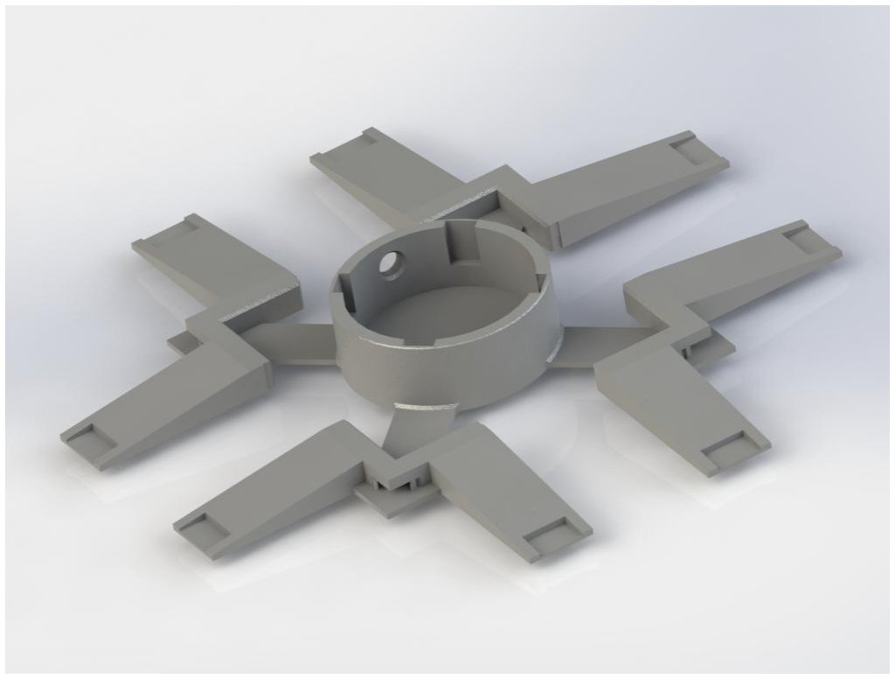
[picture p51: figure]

# Materials

1 - 3D printed MMC60 Jig
4 - 3D printed printbed adapter

## Instructions

1. Print 3D parts as stated in | the materials


2. Carefully attach one of the | adapters to the jig’s legs using the snaps
3. Repeat with other | adapters with each legs

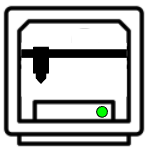
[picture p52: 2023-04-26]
Software/NeoPrint/printer_on.png

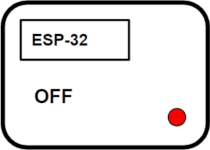
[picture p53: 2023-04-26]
Software/NeoPrint/resized_MCU_OFF.gif

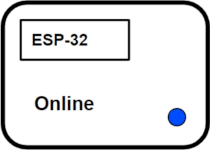
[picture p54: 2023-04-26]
Software/NeoPrint/resized_MCU_on.gif

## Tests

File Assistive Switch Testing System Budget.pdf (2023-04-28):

## Assistive Switch Testing System Budget

28/04/2023

Spending

Date | Name | Description | Supplier | Part Number | Quantity | Unit Cost (CAD) Subtotal (CAD) Link
2022/11/22 Load Cell | MINI LOAD CELL 500G STRAIGHT BAR | Digi-Key | 1568-1899-ND | 1 | $18.40 | $18.40 https://www.digikey.ca/en/products/detail/sparkfun-electronics/SEN-14728/9555602
2022/11/22 Micro USB Cable | CABLE USB A TO MICRO B | Digi-Key | 1286-1061-ND | 1 | $7.34 | $7.34 https://www.digikey.ca/en/products/detail/digilent-inc/310-053/4428835
2022/11/22 ESP32 Devkit | ESP32 WIFI BLUETOOTH EVAL BOARD | Digi-Key | 1904-1030-ND | 1 | $15.67 | $15.67 https://www.digikey.ca/en/products/detail/espressif-systems/ESP32-PICO-KIT/9381703
2022/11/22 Limit Switch | SWITCH SNAP ACTION SPDT 3A 125V | Digi-Key | SW769-ND | 1 | $2.18 | $2.18 https://www.digikey.ca/en/products/detail/omron-electronics-inc-emc-div/SS-3GPD/664730
2022/11/22 3.5mm Mono Jack | CONN JACK MONO 3.5MM R/A | Digi-Key | CP-3502MJ-ND | 1 | $2.37 | $2.37 https://www.digikey.ca/en/products/detail/cui-devices/MJ-3502/281321
2022/11/22 Male 1x5 standard HDR CONN HEADER VERT 5POS 2.54MM | Digi-Key | 609-4726-ND | 4 | $0.40 | $1.60 https://www.digikey.ca/en/products/detail/amphenol-icc-fci/69190-405HLF/4274102
2022/11/22 Load Cell Amplifier | LOAD CELL AMP HX711 | Digi-Key | 1568-1436-ND | 1 | $17.16 | $17.16 https://www.digikey.ca/en/products/detail/sparkfun-electronics/SEN-13879/6202732
2022/11/22 3.5mm Breadboard Jack STEREO JACK, ALL PLASTIC, BLACK | Digi-Key | 2092-STX-3120-3BM-ND | 1 | $1.25 | $1.25 https://www.digikey.ca/en/products/detail/kycon-inc/STX-3120-3BM/10247072
2022/11/22 3.5mm Mono Cable | CABLE R/A MONO PLUG-PLUG 6FT | Digi-Key | SC1812-ND | 1 | $12.29 | $12.29 https://www.digikey.ca/en/products/detail/switchcraft-inc/33HR07233X/1289530
2022/11/22 Digikey Order | Shipping, Tax | Digi-Key | N/A | 1 | $17.39 | $17.39
2023/01/31 Ender 3 V2 | 3D printer | 3D Printing Canada N/A | 1 | $387.22 | $387.22 https://3dprintingcanada.com/products/creality-ender-3-v2
MMC60 Switch M3x16mm Screws 2023/01/02 JLCPCB Order 2023/01/02 JLCPCB Order 2023/02/13 MMC60 Jig | 3D Printed Parts | UBC ECE N/A 1 $0.00
Hardware Lee's Electronic ShopN/A Printed Circuit Board Order JLCPCB Shipping, Tax JLCPCB 3D Printed Parts ECE | N/A N/A | 1 $1.50 $1.50 5 $0.54 $2.69 1 $26.42 $26.42 1 $41.30 $41.30
Spend Total | | $554.78

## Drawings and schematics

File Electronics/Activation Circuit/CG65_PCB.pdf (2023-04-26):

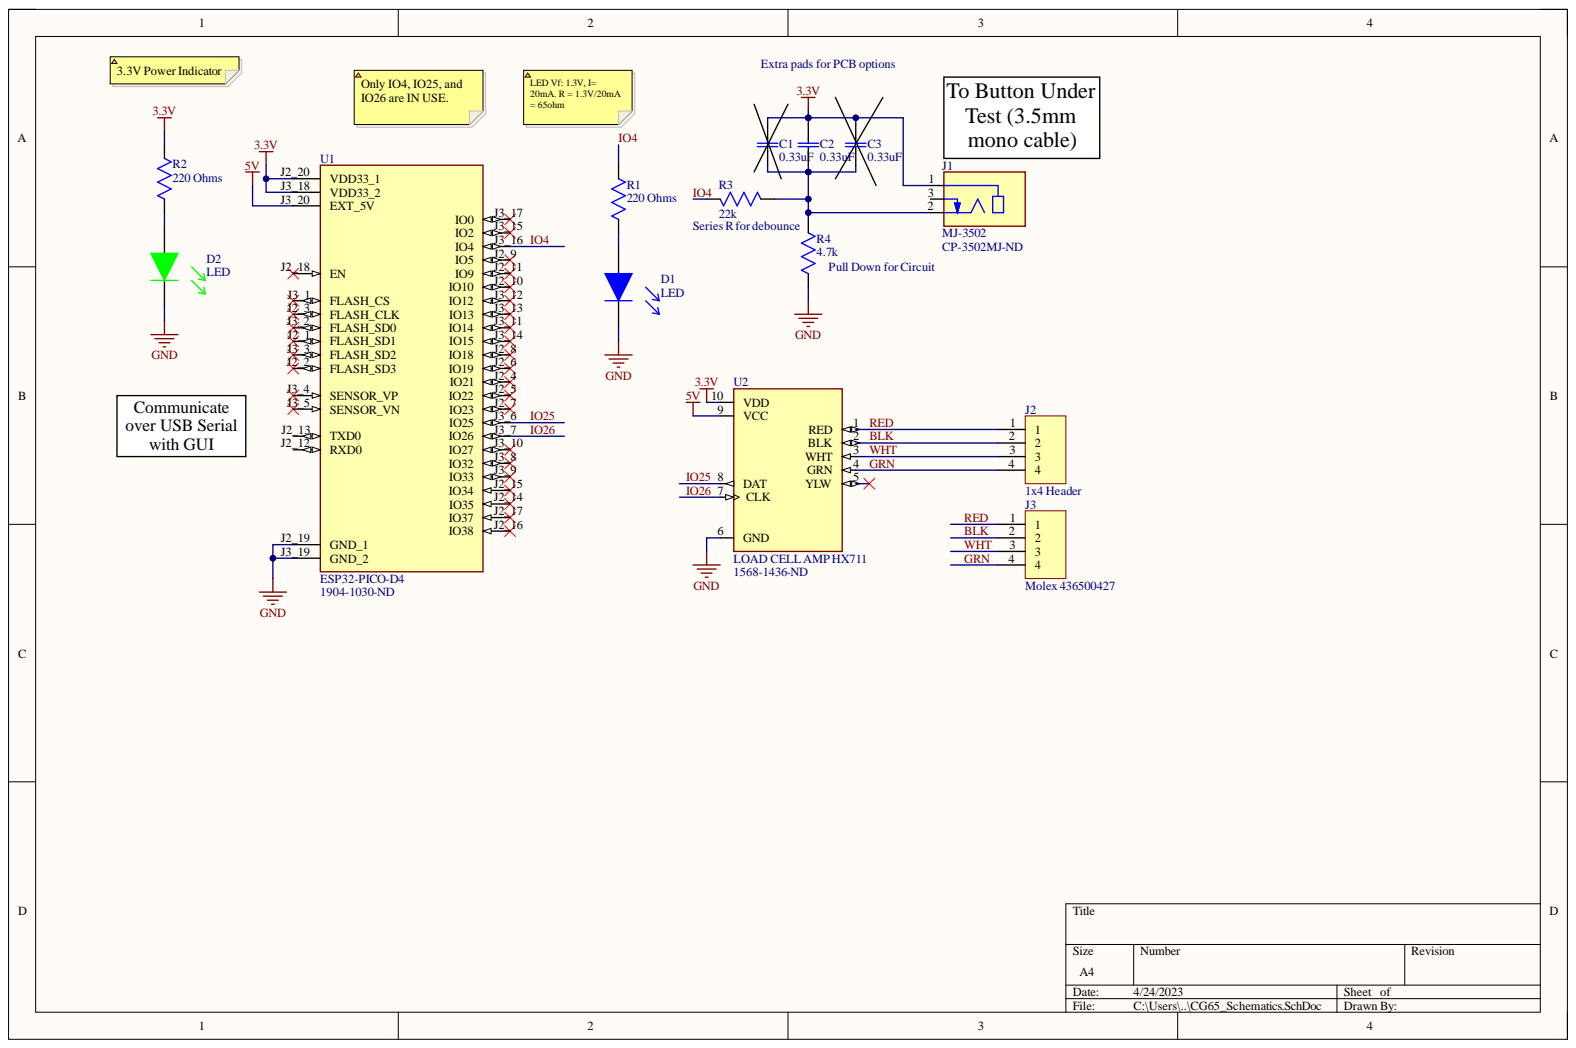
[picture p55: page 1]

To Button Under Test (3.5mm

Siz e A4 | Numb e r | R evisio n

Da te : 4/24/202 3 | She et of
File : C:\Use rs\. .\CG65_S chema ti c s . S c hD o c | Dr awn B y :

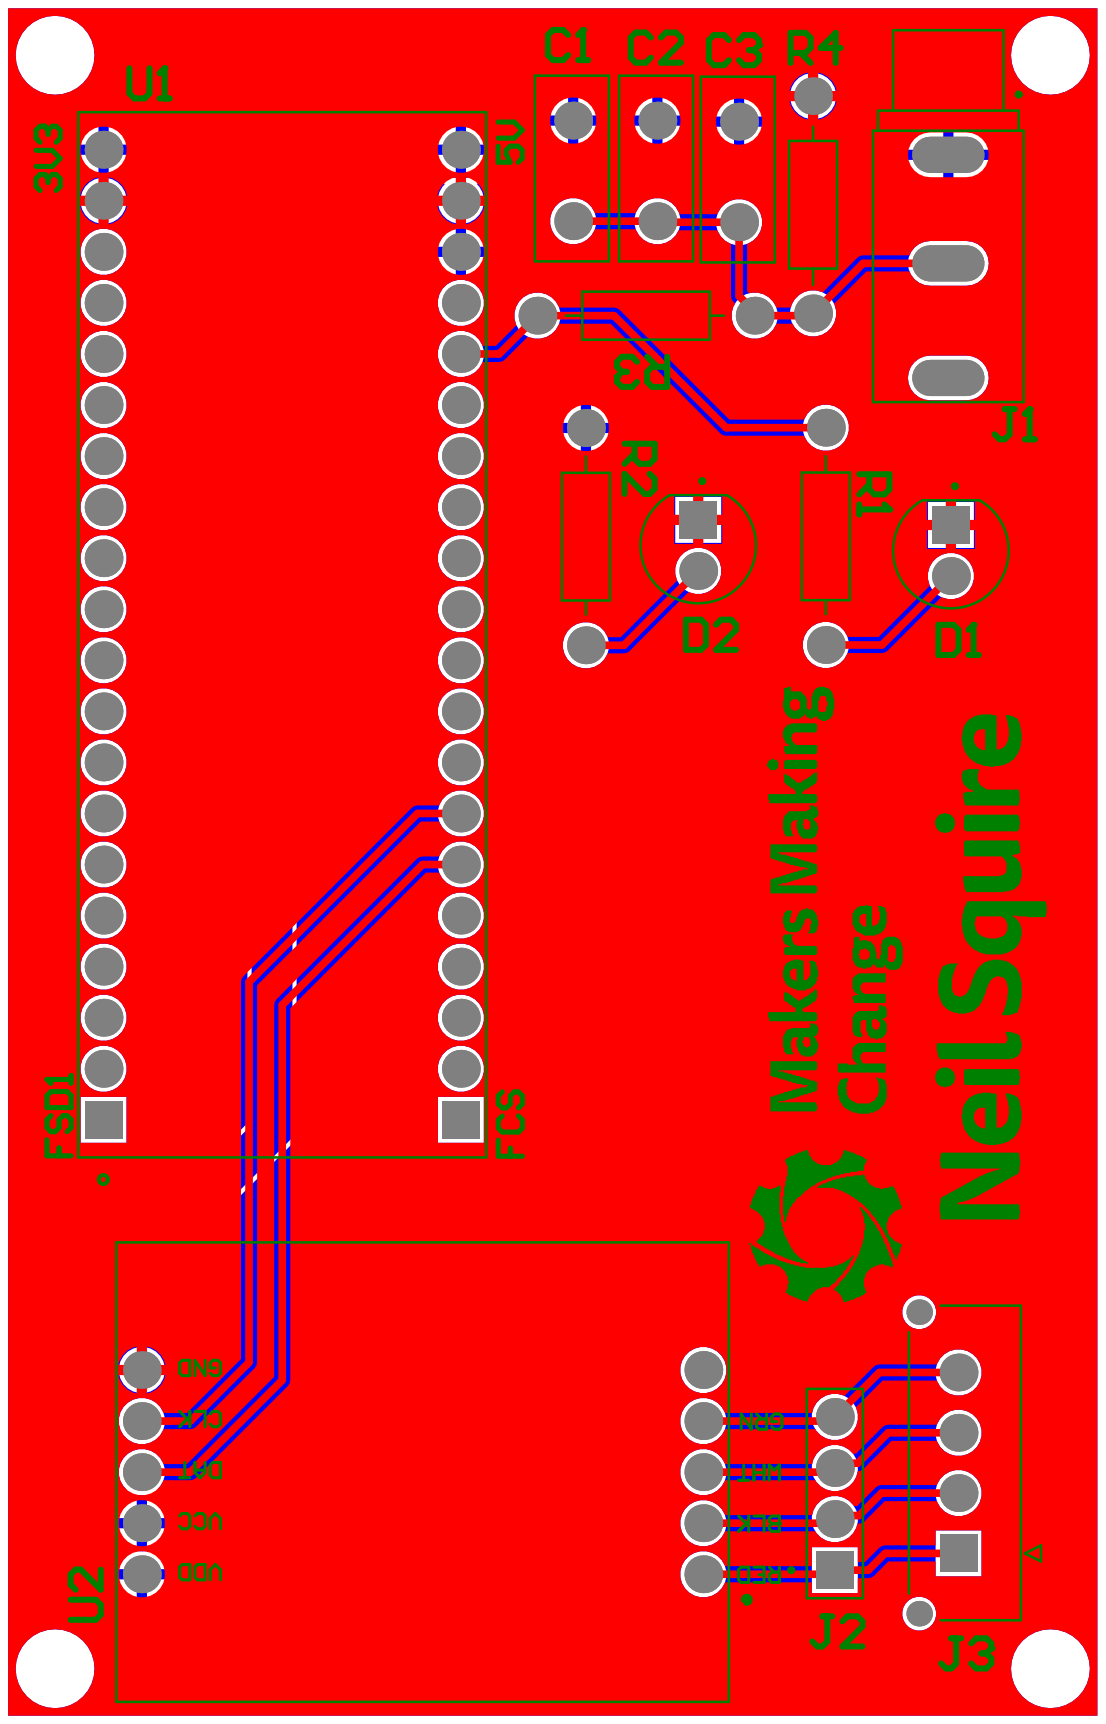
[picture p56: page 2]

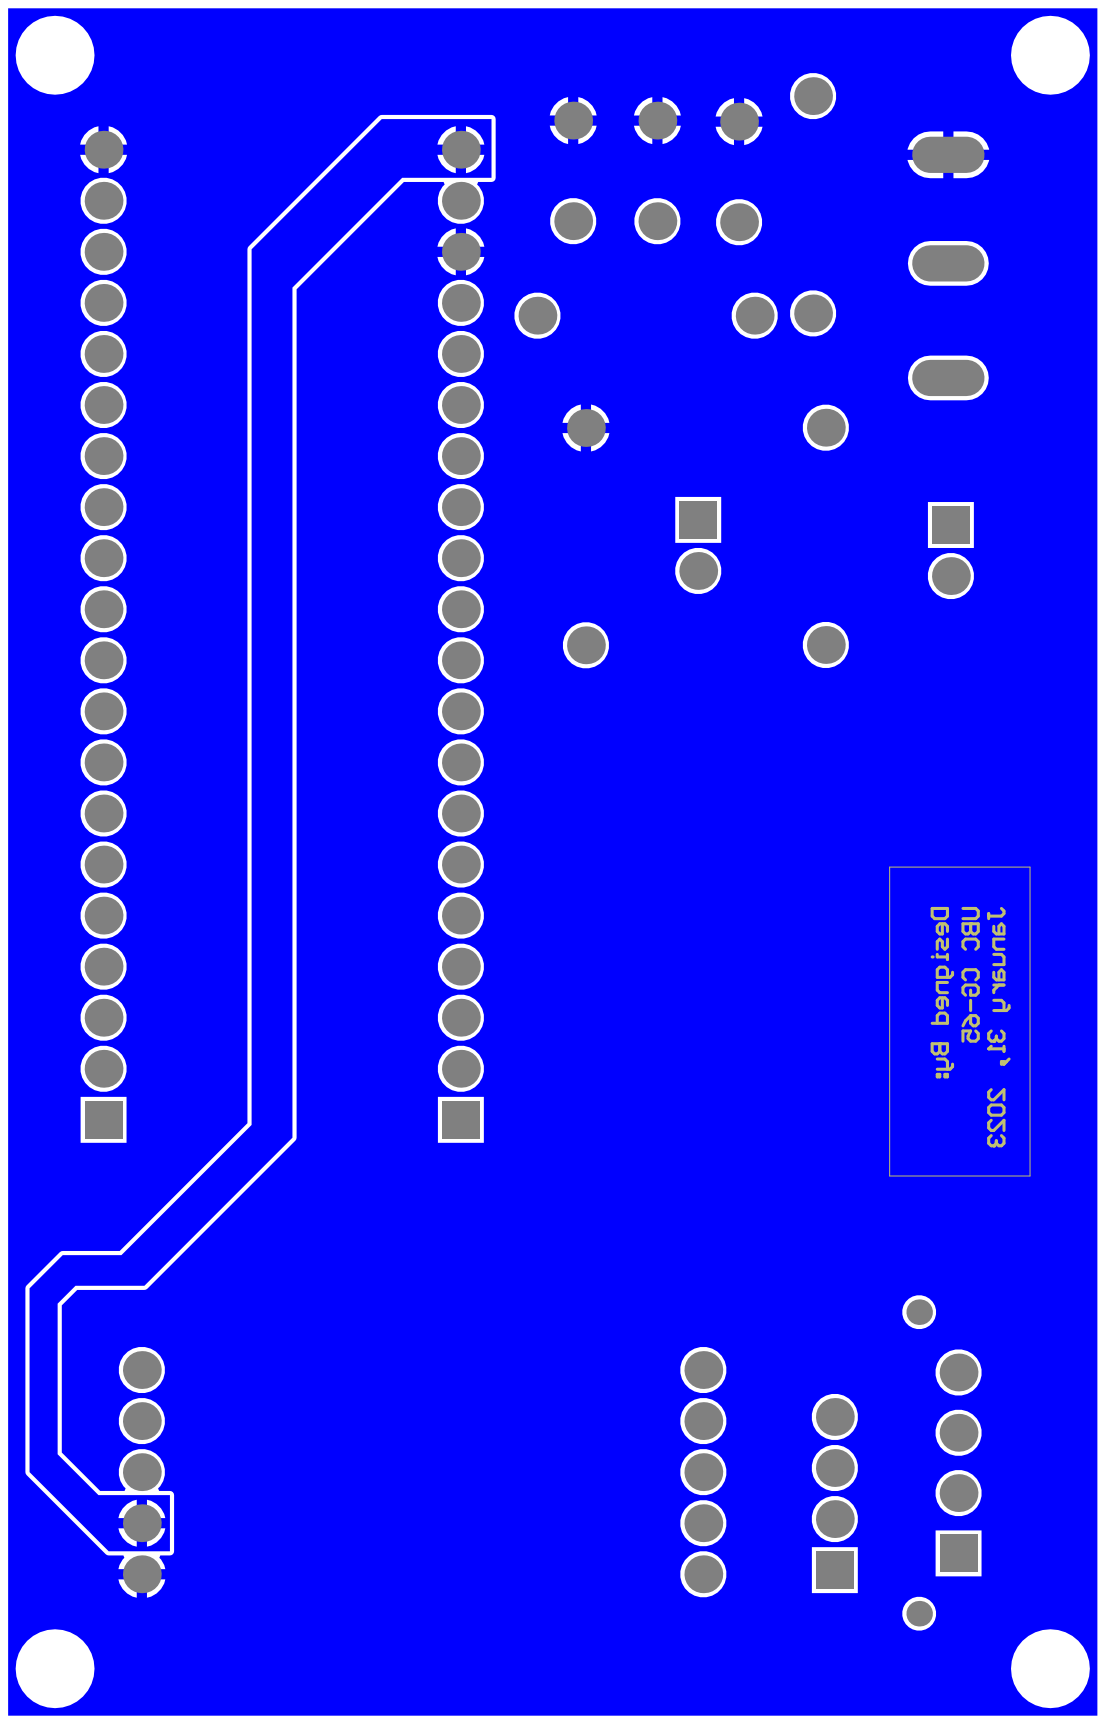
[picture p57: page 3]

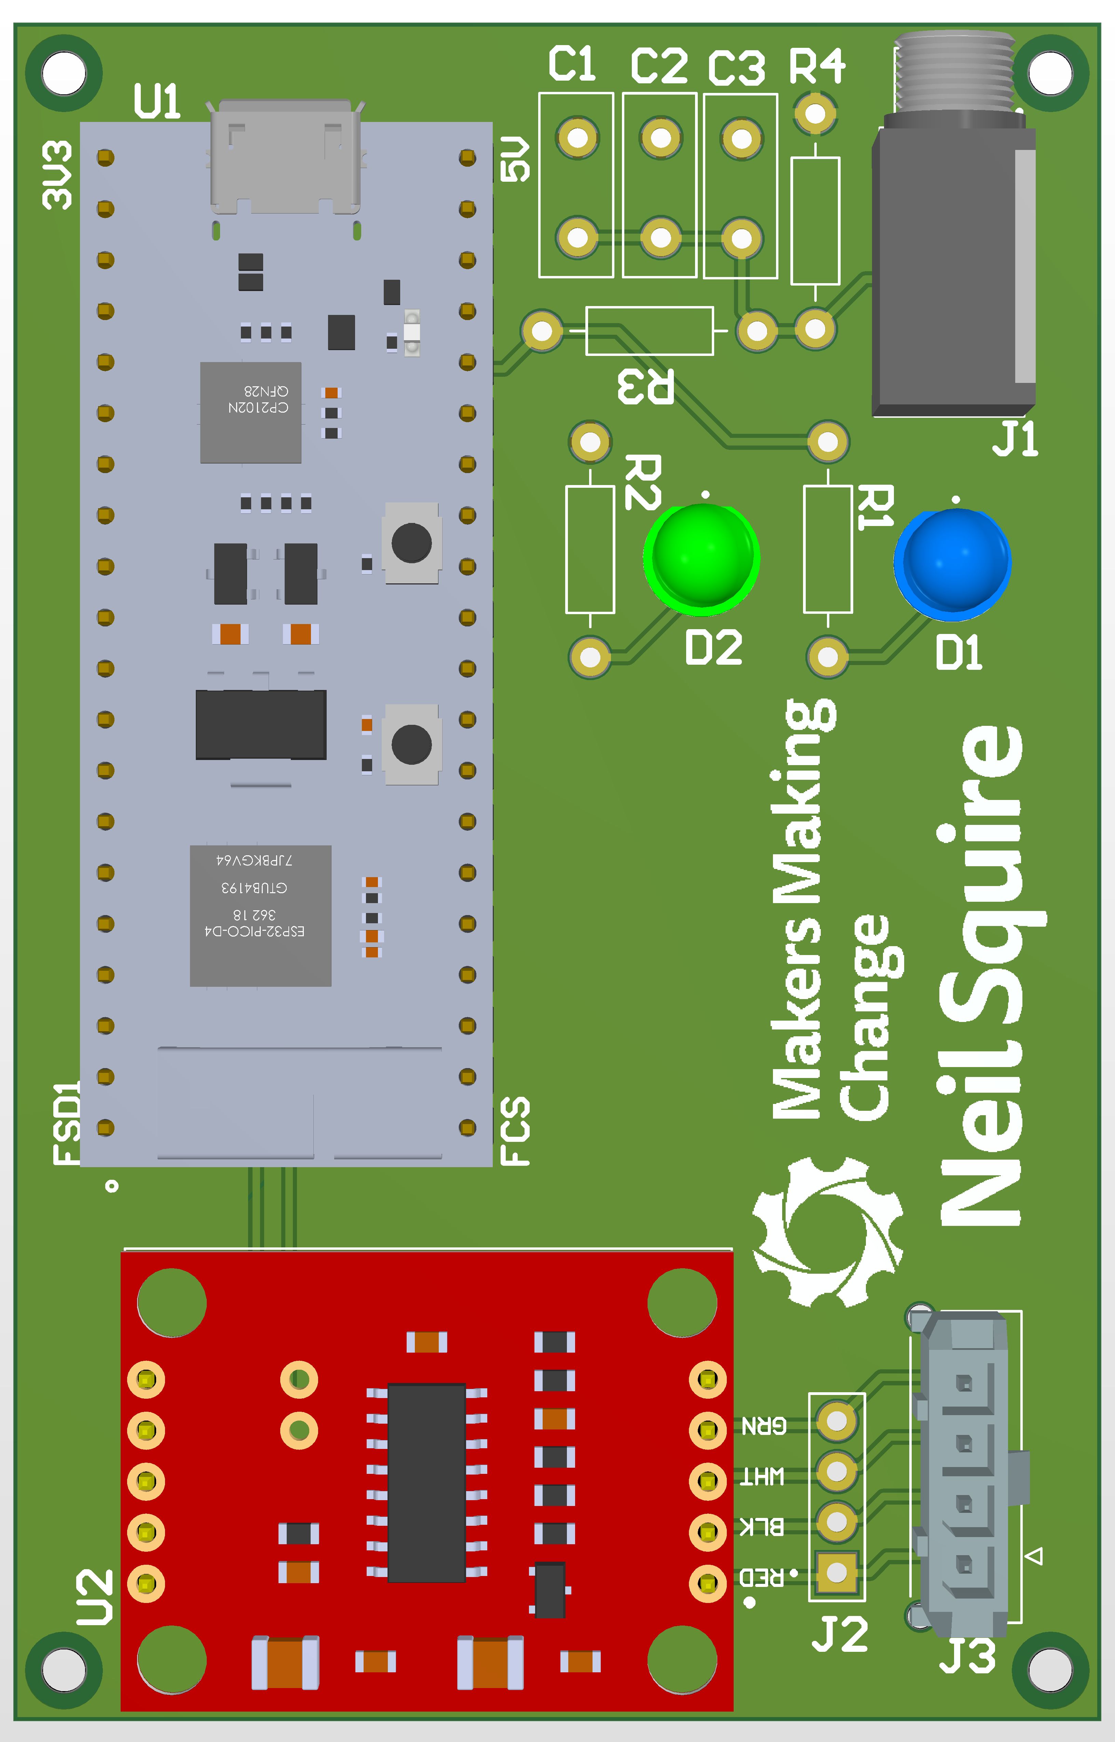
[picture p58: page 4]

Comment | Description | Designator | Footprint | LibRef | Quantity
0.33uF | Standard Capacitor, Through Hole | C1, C2, C3 | TH CAPACITOR | Capacitor | 3
LED | 2V Blue LED Through Hole | D1 | LED TH BLUE | LED Blue | 1
LED | 2V Green LED Through Hole | D2 | LED TH GREEN | LED Green | 1
MJ-3502 | 3.5 mm, Mono, Right Angle, Through Hole, Threaded Bushing, Audio Jack Connector | J1 | MJ-3502N | MJ-3502 | 1
1x4 Header | Standard 0.1" Header 1x4 | J2 | 1x4 Standard Header | 1x4 Header | 1
Molex 436500427 | Molex MicroFit 3.0 Header 1x4, mates with 0436450400 | J3 | MOLEX_436500427 | Molex 436500427 | 1
220 Ohms | Standard Resistor, Through Hole, 1/8W | R1, R2 | TH Resistor | Resistor | 2
22k | Standard Resistor, Through Hole, 1/8W | R3 | TH Resistor | Resistor | 1
4.7k | Standard Resistor, Through Hole, 1/8W | R4 | TH Resistor | Resistor | 1
ESP32-PICO-D4 | ESP32 Wifi Bluetooth Eval Board | U1 | ESP32-PICO-KIT | ESP32-PICO-KIT | 1
LOAD CELL AMP HX711 | HX711 Load Cell Amplifier | U2 | SEN-13879 | LOAD CELL AMP HX711 | 1

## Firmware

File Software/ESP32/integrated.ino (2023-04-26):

int P_SWITCH = 4; // digital pin
float grams_force;

#include "HX711.h"

double calibration_factor = 3030; // Tested on scale for validation/verification
double current_time;
double prev_time;
double rate;
double creep;

//double count;
//long randNumber; //used for testing

#define DOUT  25
#define CLK  26
#define FS 500
//#define zero -57598
// creep 0.000036 g / ms
HX711 scale;

void setup() {
  // put your setup code here, to run once:
  pinMode(P_SWITCH, INPUT);
  //Serial.begin(9600);
  Serial.begin(115200); // May need to run at a faster baud rate if the data is inaccurate (Only did static force tests, rather than dynamic as the probe is moving type of test)


//comment if no electronics

  scale.begin(DOUT, CLK);
  
  scale.set_scale(calibration_factor); //This value is obtained by using the SparkFun_HX711_Calibration sketch
  scale.tare(); //Assuming there is no weight on the scale at start up, reset the scale to 0


  current_time = 0;
  prev_time = 0;
  creep = 0.05*500.0 *(1/3.0)*(1/60.0)*(1/1000.0)*10; // %FS / 3min * 1min/60s = creep in g /10ms

  //count = 0; //only used as dummy data


}

void loop() {
  // put your main code here, to run repeatedly:

  //randNumber = random(0,100);
  //grams_force = 2; //randNumber; //use if no electronics
  grams_force = scale.get_units(); //comment out if no electronics
  current_time = millis();
  if (current_time - prev_time >= 10) {
    prev_time = millis();
    grams_force -= creep;
  }
/* FORMAT of data sent to GUI
* Button's activation status: "0" OR "1"
* semicolon: ";"
* measured force: [float]
* semicolon: ";"
* measured distance: (float)
* semiconlon: ";"
* position: (char)
*/


  Serial.print(digitalRead(P_SWITCH)); //comment out if there's not electronics connected

  Serial.print(";");
  
  //Serial.print(" Grams-Force: ");
  Serial.print(grams_force, 1);

/*
  Serial.print(";");

  //Serial.print(" Distance: ");
  randNumber = random(1,11);

  Serial.println();
*/
//  count += 0.1;

//  delay(1000);
  Serial.println();
}

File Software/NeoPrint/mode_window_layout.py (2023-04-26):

'''
Import
'''
import sys
import time
import threading
import serial
import math
import re
from PyQt6.QtCore import QTimer
from PyQt6.QtGui import QAction
from PyQt6.QtGui import QMovie

from PyQt6.QtWidgets import QApplication, QMainWindow, QWidget, QLabel, QComboBox, QGroupBox,  \
    QPushButton, QHBoxLayout, QVBoxLayout, QTextEdit, QMenuBar, QDialog, QDialogButtonBox, QFormLayout, QRadioButton, QMenu
import matplotlib.pyplot as plt
from matplotlib.backends.backend_tkagg import FigureCanvasTkAgg
from matplotlib.figure import Figure
from matplotlib.backends.backend_qt5agg import FigureCanvasQTAgg as FigureCanvas

import pyqtgraph as pg
import numpy as np
from scipy.ndimage import gaussian_filter
from matplotlib.patches import Circle

import tkinter

BUTTON_MAX_COORD = 60 #assuming circular button

#from areamode import AreaModeFunc

class HeatmapWidget(QWidget):

    def __init__(self, data_type, parent=None):
        super().__init__(parent)
        self.data_type = data_type
        self.data = []  # initialize data as an empty array
        self.init_heatmap()

        # Create a Figure and add it to a FigureCanvas
        self.fig = Figure()
        self.canvas = FigureCanvas(self.fig)
        self.window_size = 60

        # Create axis, circle, and colorbar only once
        self.ax = self.fig.add_subplot(1, 1, 1)
        self.circle = Circle((self.window_size / 2, self.window_size / 2),
                             radius=self.window_size / 2, edgecolor='black', facecolor='none')
        self.ax.add_patch(self.circle)
        self.colorbar = None

        # Draw the heatmap on the canvas
        self.draw_heatmap()

        layout = QVBoxLayout(self)
        layout.addWidget(self.canvas)

    def init_heatmap(self):
        global BUTTON_MAX_COORD

        self.window_size = 60
        self.heatmap = np.zeros((self.window_size, self.window_size))

        for x, y, activation_distance, activation_force in self.data:
            xi, yi = self.normalize_coordinates(x, y)  # Normalize the x and y coordinates here
            xi, yi = int(xi), int(yi)
            if self.data_type == 'force':
                weight = float(activation_force) * self.window_size / max(
                    [float(point[3]) for point in self.data])  # Convert to float
            elif self.data_type == 'distance':
                weight = float(activation_distance) * self.window_size / max(
                    [float(point[2]) for point in self.data])  # Convert to float
            self.heatmap[yi, xi] += weight

        self.sigma = 10
        self.smoothed_heatmap = gaussian_filter(self.heatmap, self.sigma)

        y, x = np.ogrid[-self.window_size // 2:self.window_size // 2, -self.window_size // 2:self.window_size // 2]
        self.mask = x ** 2 + y ** 2 <= (self.window_size // 2) ** 2

    def update_heatmap(self, data_array):
        # Normalize the x and y coordinates and convert activation_distance and activation_force to float
        self.data = data_array
        self.init_heatmap()
        self.draw_heatmap()

    def draw_heatmap(self):
        self.ax.clear()

        colormap = plt.get_cmap('YlOrBr')
        image = colormap(self.smoothed_heatmap)
        image[~self.mask, 3] = 0

        heatmap = self.ax.imshow(image, origin='lower', extent=[0, self.window_size, 0, self.window_size], aspect='auto',
                                 cmap=colormap)

        if self.colorbar is None:
            self.colorbar = self.fig.colorbar(heatmap)
        else:
            self.colorbar.update_normal(heatmap)

        self.colorbar.set_label('Activation Force' if self.data_type == 'force' else 'Activation Distance')

        if self.data:  # Check if self.data is not empty
            activation_distances = [point[2] for point in self.data]
            activation_forces = [point[3] for point in self.data]
            normalized_distances = np.interp(activation_distances,
                                             (min(activation_distances), max(activation_distances)),
                                             (0, 1))
            normalized_forces = np.interp(activation_forces, (0, max(activation_forces)), (0, 1))

            for i, (x, y, _, _) in enumerate(self.data):
                xi, yi = self.normalize_coordinates(x, y)
                if self.data_type == 'force':
                    self.ax.scatter(xi, yi, color=colormap(normalized_forces[i]), s=125, edgecolors='black', marker='o')
                else:
                    self.ax.scatter(xi, yi, color=colormap(normalized_distances[i]), s=125, edgecolors='black', marker='o')

        self.ax.add_patch(self.circle)

        self.ax.set_title('Activation Heatmap - ' + ('Force' if self.data_type == 'force' else 'Distance'))
        self.ax.set_xlabel('X Coordinate')
        self.ax.set_ylabel('Y Coordinate')
        self.ax.set_facecolor((0, 0, 0, 0))



        self.canvas.draw()

    def normalize_coordinates(self, x, y):
        max_coord = 300
        new_center = [133.5, 119.8]
        return ((x - new_center[0] + BUTTON_MAX_COORD / 2), (y - new_center[1] + BUTTON_MAX_COORD / 2))



class SingleModeWindow(QWidget):
    def __init__(self, parent=None):
        super().__init__(parent)

        self.serial = None
        self.ESPserial = None
        self.location = None  # Initialize location variable
        self.location_lock = threading.Lock()
        self.button_not_pressed = True
        self.point_coords = None

        #self.gf = general_function
        self.force_data = None
        self.distance_data = None
        self.activation = None
        self.on_surface = False
        self.current_z = None

        self.local_increment_record = None
        self.local_increment_list = []
        self.z_activation = None
        self.z_activation_list = []

        self.surface_z = None

        #################
        self.status = {
            'printer': 'Offline',
            'microcontroller': 'Offline',
        }
        #################
# 4/22
        self.x_input = None
        self.y_input = None

        #################

        self.init_ui()

    def init_ui(self):
        main_layout = QHBoxLayout(self)

        # Create left layout
        left_layout = QVBoxLayout()

        # Group 3D printer and microcontroller layouts in separate QGroupBoxes
        printer_groupbox = QGroupBox("3D Printer")
        microcontroller_groupbox = QGroupBox("Microcontroller")

        printer_layout = self.create_printer_layout()
        microcontroller_layout = self.create_microcontroller_layout()

        printer_groupbox.setLayout(printer_layout)
        microcontroller_groupbox.setLayout(microcontroller_layout)

        left_layout.addWidget(printer_groupbox)
        left_layout.addWidget(microcontroller_groupbox)

        # Add left layout to the main layout
        main_layout.addLayout(left_layout)

        # Create right layout
        right_layout = QVBoxLayout()

        # Add status layout
        status_groupbox = QGroupBox("Status")
        status_layout = self.create_status_layout()
        status_groupbox.setLayout(status_layout)
        right_layout.addWidget(status_groupbox)

        # Add test result text
        self.test_result_label = QLabel('Test Result:')
        right_layout.addWidget(self.test_result_label)

        self.test_result_textedit = QTextEdit()
        self.test_result_textedit.setReadOnly(True)
        right_layout.addWidget(self.test_result_textedit)

        # Add right layout to the main layout
        main_layout.addLayout(right_layout)

        self.setWindowTitle('NeoPrint - Single Mode')
        self.resize(400, 200)

    def display_test_results(self):
        results_str = ''
        for point in self.point_coords:
            x_coord = point[0]
            y_coord = point[1]
            activation_distance = point[2]
            activation_force = point[3]
            point_str = f"x_coord: {x_coord}\n" \
                        f"y_coord: {y_coord}\n" \
                        f"activation_distance: {activation_distance:.2f}\n" \
                        f"activation_force: {activation_force}\n\n"
            results_str += point_str
        self.test_result_textedit.setText(results_str)

    def create_printer_layout(self):

        # Create 3D printer layout
        printer_layout = QVBoxLayout()

        printer_layout.setSpacing(10)

        # Create button layout
        button_layout = QHBoxLayout()
        button_label = QLabel('Button Model:')
        button_layout.addWidget(button_label)
        self.button_combo = QComboBox()
        self.button_combo.addItems(['Button Profile 1', 'Button Profile 2'])
        button_layout.addWidget(self.button_combo)
        self.test_button = QPushButton('Test')
        self.test_button.clicked.connect(self.TEST)
        button_layout.addWidget(self.test_button)
        printer_layout.addLayout(button_layout)





# 4/22
################################
        # Create switch location input layout
        switch_location_layout = QHBoxLayout()

        self.switch_location_label = QLabel('Switch location (x, y):')
        switch_location_layout.addWidget(self.switch_location_label)

        self.x_input = QTextEdit(self)
        self.x_input.setMaximumHeight(28)
        self.x_input.setMaximumWidth(80)
        switch_location_layout.addWidget(self.x_input)

        self.y_input = QTextEdit(self)
        self.y_input.setMaximumHeight(28)
        self.y_input.setMaximumWidth(80)
        switch_location_layout.addWidget(self.y_input)

        self.generate_button = QPushButton('Generate')
        self.generate_button.clicked.connect(self.click_to_generate_points)
        switch_location_layout.addWidget(self.generate_button)

        printer_layout.addLayout(switch_location_layout)

        # Create Test button
        self.TESTbutton = QPushButton('TESTBY')
        self.TESTbutton.clicked.connect(self.TEST)
        switch_location_layout.addWidget(self.TESTbutton)
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

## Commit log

2023-04-25 Create 3D Printing Files
2023-04-25 Added files to 3D Printing Files
    [InteractJigV2.SLDPRT, InteractJigV2.STL, JigPrintbedAdapter.SLDPRT, JigPrintbedAdapter.STL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]
2023-04-25 Deleted files under hardware
    Hardware folders divided into two: 3D Printing Files and Electronics
    [InteractJigV2.SLDPRT, InteractJigV2.STL, JigPrintbedAdapter.SLDPRT, JigPrintbedAdapter.STL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]
